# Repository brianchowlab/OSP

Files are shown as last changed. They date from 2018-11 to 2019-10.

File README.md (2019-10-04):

# OSP: An Open-source Plate Reader 
<p align="center">
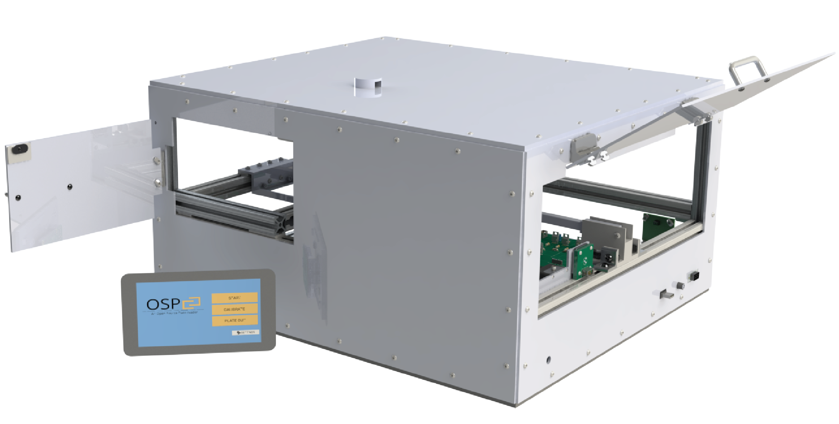
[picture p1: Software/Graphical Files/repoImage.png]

</p>

## Introduction
OSP is a low-cost open-source plate reader built out of the [Chow Lab](http://chowlab.seas.upenn.edu/) and the [George H. Stephenson Foundation Bioengineering Educational Laboratory & Bio-MakerSpace](https://belabs.seas.upenn.edu/) at the University of Pennsylvania. The software provided in this repository is required to access the full functionailty of a built OSP device. For information regarding how to build this device and details about how it works, please refer to the ACS: BioChemistry manuscript available at this [LINK](https://www.biorxiv.org/content/early/2018/09/12/413781).

## Contents
The repository is divided into two main components: (1) Hardware & (2) Software
        
* [**HARDWARE**](https://github.com/brianchowlab/OSP/tree/master/Hardware)

    All the files required for assembly of the OSP device are in this folder. All the instructions on how to assemble the OSP device can be found in the *ASSEMBLY FILES* directory.
  * [***CAD FILES***](https://github.com/brianchowlab/OSP/tree/master/Hardware/CAD%20Files)
  * [***LASER CUT FILES***](https://github.com/brianchowlab/OSP/tree/master/Hardware/Laser%20Cut%20Files)
  * [***PCB FILES***](https://github.com/brianchowlab/OSP/tree/master/Hardware/PCB%20Files)
  * [***ASSEMBLY FILES***](https://github.com/brianchowlab/OSP/tree/master/Hardware/Assembly%20Files)
* [**SOFTWARE**](https://github.com/brianchowlab/OSP/tree/master/Software)

    All the files for installation and execution of the OSP software are in this folder. The full *Software Guide* can be found here as a PDF.
  * [***ARDUINIO FILES***](https://github.com/brianchowlab/OSP/tree/master/Software/Arduino%20Files/OSP_Serial_Communication/COPR_Serial_Communication)
  * [***GRAPHICAL FILES***](https://github.com/brianchowlab/OSP/tree/master/Software/Graphical%20Files)
  * [***PYTHON FILES***](https://github.com/brianchowlab/OSP/tree/master/Software/Python%20Files)
    * Data - Folder where all data from the OSP device is saved as .xlsx files.
    * Protocols - Folder where any protocol sequence is saved. 
    * Screens - Python files for all GUI screens
    * System Settings - Folder where are all files associated with settings are contained.
    * Raspberry Pi Image - Contains the link to the Raspberry-Pi image file.

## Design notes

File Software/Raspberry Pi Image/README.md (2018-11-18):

# OSP: An Open-source Plate Reader 

## RASBPERRY PI IMAGE - LINK BELOW 

[DISK IMAGE FILE (Updated Nov. 18, 2018)](https://www.dropbox.com/s/7g2e63knupe5y7j/osp_rasp.img?dl=0)

## Instructions for referrence:

### Installation (Raspberry-Pi Image)
The simplest way to install the OSP software on a Raspberry-Pi is by downloading and installing the OSP.img file provided. In order to do this, you will need to have a completely empty 16GB Micro SD Card. If the card is not empty, all of its contents will be deleted in the installation of the OSP.img file. In addition, the first 3 installation steps need to be performed on a computer/laptop with an SD card slot. 

**Step 1.** *Download & Unzip the OSP.img* - Visit the following [LINK](https://www.dropbox.com/s/7g2e63knupe5y7j/osp_rasp.img?dl=0) and download the *OSP.img* file. Once downloaded unzip the file to a known location. 

**Step 2.** *Download & Install the Etcher program* - Visit the following [LINK](https://www.balena.io/etcher/) and download the *Etcher* program for your specific operating system. 

**Step 3.** *Install the OSP.img onto the SD Card* - Insert your empty SD card into the computer. Start up the Etcher software and follow the on screen instructions in order to install the OSP.img onto the card. **This process can take up to 10 minutes**

**Step 4.** *Update OSP repository* - Once the OSP.img file is installed, insert it into your Raspberry-Pi (which should be connected to the active OSP device, touch-screen/monitor, keyboard & mouse). Turn the Raspberry-Pi on and when it is booted open up the Terminal. Type the following and close the Terminal when it is finished:
```sh
$ cd OSP
$ git pull origin master
```
**Step 5.** *Running the Usert Interface* - To activate the User Interface make sure the OSP device is turned on and connected to the Raspberry-Pi via USB. Open up the Terminal and type the following:
```sh
$ cd  "OSP\Software\Python Files"
$ sudo python GUI.py
```
## SOFTWARE - Before Running a Protocol

### Initial Functionality Testing
Once you have completed the installation process (by following the steps above) it is usefull to check if all the light sources (LEDs) and linear actuators as behaving correctly. These tests can be performed from the Arduino IDE *Serial Monitor*. 

**Step 1.** *Open Arduino Serial Monitor* - Make sure the OSP device is plugged into a computer/Raspberry-Pi and turned on. Open up the Arduino IDE and click on the ***Tools*** tab in the menu bar. From the dropdown menu select ***Serial Monitor***. This will open up the ***Serial Monitor*** in a new window. 

**Step 2.** *Test Linear Actuator Functionality* 
* Type the following into the text box at the top of the Serial Monitor and press the *Send* button: **M1500.001500.00;** 
  * This should extend both linear actuators about half way. 
* Type the following into the text box at the top of the Serial Monitor and press the *Send* button: **M1000.001000.00;** 
  * This should retract both linear actuators all the way. 
  
**Step 3.** *Test LED Functionality* 
* Type the following into the text box at the top of the Serial Monitor and press the *Send* button: **L1;** 
  * This should result in the LED 1 turning on. To turn it off, type the same command in again.   
* Type the following into the text box at the top of the Serial Monitor and press the *Send* button: **L2;** 
  * This should result in the LED 2 turning on. To turn it off, type the same command in again.   
* Type the following into the text box at the top of the Serial Monitor and press the *Send* button: **L3;** 
  * This should result in the LED 3 turning on. To turn it off, type the same command in again.
* Type the following into the text box at the top of the Serial Monitor and press the *Send* button: **L4;** 
  * This should result in the LED 4 turning on. To turn it off, type the same command in again.
* Type the following into the text box at the top of the Serial Monitor and press the *Send* button: **L5;** 
  * This should result in the LED 5 & LED 6 (top) turning on. To turn them off, type the same command in again.
  
### Calibration Guide
The software provided in this repository comes with pre-loaded with calibrated positions for a 24-well plate and a 96-well plate. However, it is recommended that an initial calibration is performed after the OSP device is built to account for any small differences in assembly. 

Before performing any sort of calibration you will need to prepare the calibration lid for the specific plate-type that is to be calibrated. Refer to the *Calibration Lid Assembly* at the end of the *General Assembly Guide* for instructions on how to do this.

The following steps should be followed everytime a calibration is performed:

**Step 1.** *Attach Fiber to Photodiode* - Deattach the fiber from the STS spectrophotometer and screw it into the photodiode mount rigth next to it. 

**Step 2.** *Adjust the Iris* -  As part of the Top Optics assembly there is an iris. Using the guidelines on the rim of the iris, set the iris to a size of 2. 

**Step 3.** *Insert plate into OSP device* - Place the calibration lid onto an empty micro-well plate and insert it into the device, such that well A1 is in the top left corner of the plate holder. (To move the plate holder near the door, press the *plate out* button on the GUI). 

**Step 4.** *Initialize calibration* - On the GUI press the *Calibrate* button and when prompted input the size of the micro-well plate (24 or 96). The machine will begin the calibration process and alert you when it is finished. **This process takes around 3 minutes**

### Loading a Plate

The orientation in which you load the plate is important not only for the calibration process but also for any sort of measurement performed on the OSP device. Please refer to the below picture to ensure you are loading the plate correctly.  The plate should be held firmly in place with attached springs. 
<p align="center">
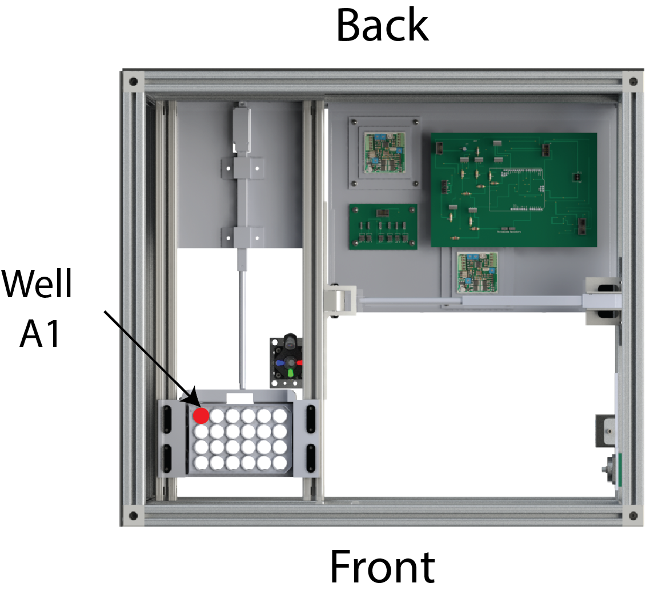
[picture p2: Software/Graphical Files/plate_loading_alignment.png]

</p>

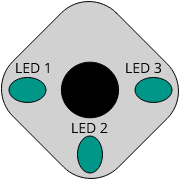
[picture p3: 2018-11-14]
Software/PythonFiles/Images/botttomLed.png

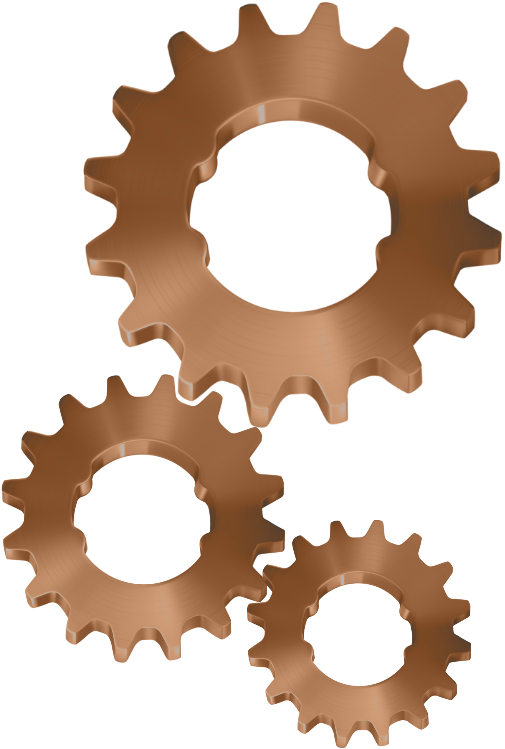
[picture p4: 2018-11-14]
Software/PythonFiles/Images/copr_gears.png

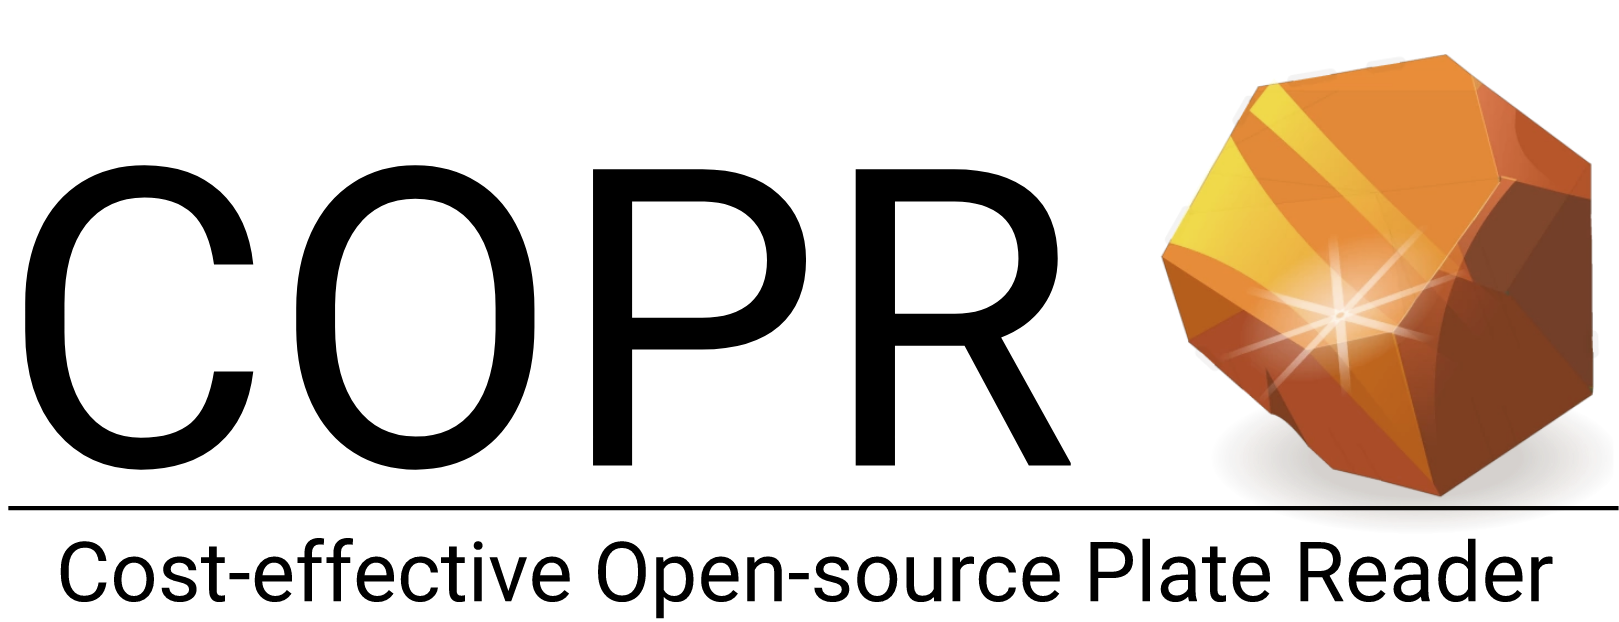
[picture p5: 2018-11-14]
Software/PythonFiles/Images/Page 3.png

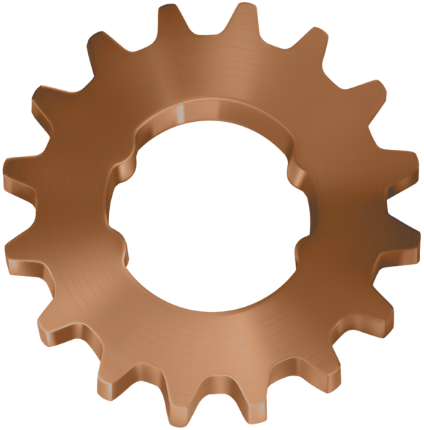
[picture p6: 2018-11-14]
Software/PythonFiles/Images/copr_gears_v2.png

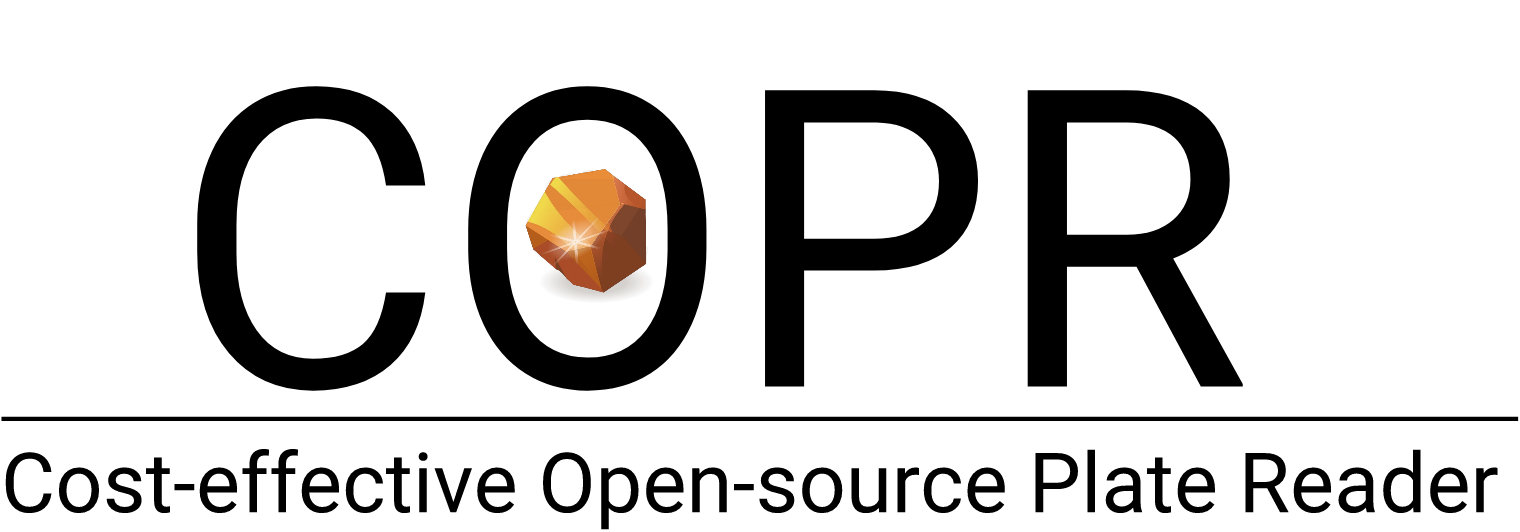
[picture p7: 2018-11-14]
Software/PythonFiles/Images/Page 6.png

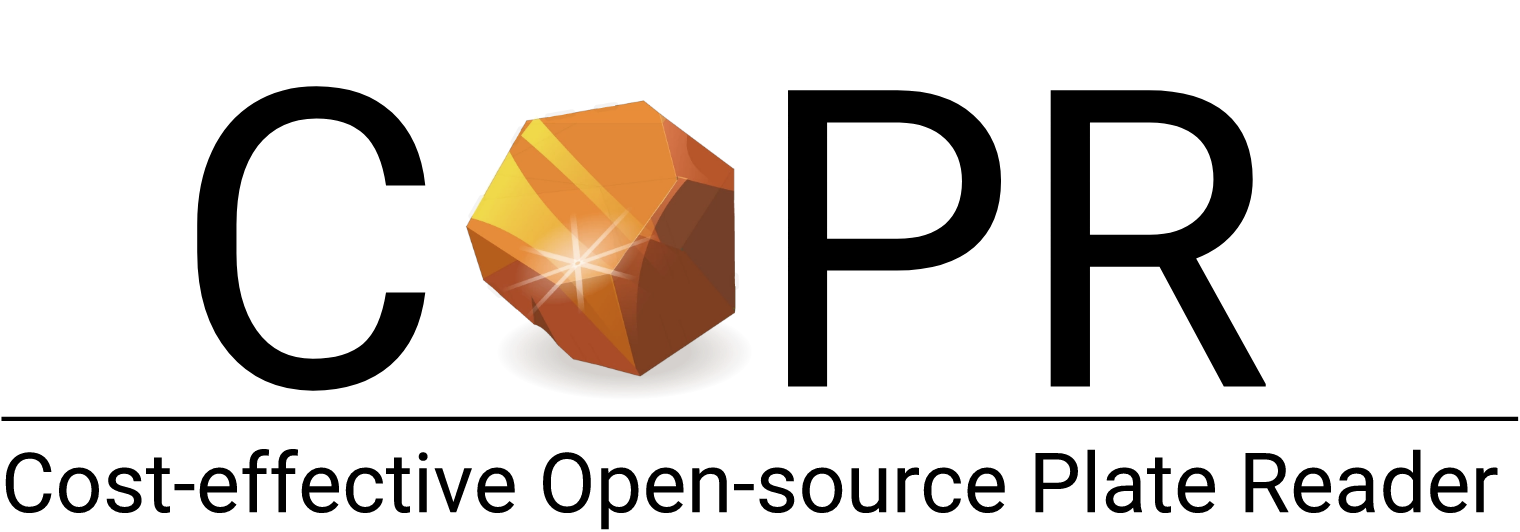
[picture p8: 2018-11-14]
Software/PythonFiles/Images/Page 5.png

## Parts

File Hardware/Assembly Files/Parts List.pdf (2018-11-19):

TABLE S1. OSP component list and costs. The total instrument cost is <$3,500. Laser cut and 3D-printed costs are reflected in material costs.
Key: Blue = optics (O). Gray = Frame (F). Orange = Electronics (E). Green = Laser Cut (L). Pink = 3D Print (P).
# | Vendor | Part Description | Part / Model Number | Unit cost | Number | Line subtotal

O1 | Thorlabs | Universal Base Plate, 2.5" x 2.5" x 3/8" | UBP2 | $36.47 | 2 | $72.94
O2 | Thorlabs | Cage Assembly Rod, 4" Long, Ø6 mm | ER4 | $7.10 | 1 | $7.10
O3 | Thorlabs | Cage Assembly Rod, 3" Long, Ø6 mm | ER3 | $6.60 | 1 | $6.60
O4 | Thorlabs | SM1-Threaded 30 mm Cage Plate, 6 mm Thick | CP6S | $19.16 | 2 | $38.32
O5 | Thorlabs | Aspheric Condenser Lens, Ø12 mm, f=10.5 mm, NA=0.54, Uncoated | ACL1210U | $18.05 | 2 | $36.10
O6 | Thorlabs | SM05 Lens Tube, 0.50" Thread Depth, One Retaining Ring Included | SM05L05 | $14.10 | 3 | $42.30
O7 | Thorlabs | Adapter with External SM1 Threads and Internal SM05 Threads, Knurled Edge | SM1A6FW | $19.99 | 2 | $39.98
O8 | Thorlabs | SM1 Graduated Ring-Actuated Iris Diaphragm (Ø1 - Ø12 mm) | SM1D12C | $103.02 | 1 | $103.02
O9 | Thorlabs | SM1 Lens Tube, 2" Thread Depth, One Retaining Ring Included | SM1L20 | $16.50 | 1 | $16.50
O10 | Thorlabs | LED Socket | 8060-2 | $9.89 | 5 | $49.45
O11 | Thorlabs | SM05-Threaded Mount for TO-18, TO-39, TO-46, or T-1 3/4 LEDs | S05LEDM | $32.64 | 1 | $32.64
O12 | Thorlabs | SMA Fiber Adapter Plate with External SM1 (1.035"-40) Thread | SM1SMA | $29.58 | 2 | $59.16
O13 | Thorlabs | SM1-Threaded Aluminum Mount for TO-5 Laser Diodes | S1LM05 | $36.47 | 1 | $36.47
O14 | Thorlabs | LED with a Glass Lens, 430 nm, 8 mW, TO-18 | LED430L | $11.73 | 1 | $11.73
O15 | Thorlabs | Epoxy-Encased White Light LED, 13.0 mW, 7.5° Half Viewing Angle, Qty. of 5 | LEDWE-15 | $9.38 | 1 | $9.38
O16 | Thorlabs | 543 nm, f = 7.86 mm, NA = 0.51 SMA905 Fiber Collimation Pkg. | F240SMA-A | $150.96 | 1 | $150.96
O17 | Thorlabs | 1/4"-20 Low-Profile Channel Screws (100 Screws/Box) | SH25LP38 | $23.66 | 1 | $23.66
O18 | Thorlabs | Drop-In T-Nut, 1/4"-20 Tapped Hole | XE25T1 | $29.33 | 1 | $29.33
O19 | Thorlabs | Si Photodiode, 10 ns Rise Time, 350 - 1100 nm, 3.6 mm x 3.6 mm Active Area | FDS100 | $14.08 | 1 | $14.08
O20 | Thorlabs | SM05 Lens Tube, 2" Thread Depth, One Retaining Ring Included | SM05L20 | $20.60 | 1 | $20.60
O21 | Thorlabs | OEM Flange to Internal SM1 Adapter, 10 mm Thread Depth | SM1F1 | $19.18 | 1 | $19.18
O22 | LED Supply | 5mm LED - Blue 470nm 15 Degree Viewing Angle | L1-0-B5TH15-1 | $0.47 | 1 | $0.47
O23 | LED Supply | 5mm LED - Orange 610nm 30 Degree Viewing Angle | L4-0-O5TH30-1 | $0.60 | 1 | $0.60
O24 | LED Supply | 5mm LED - Green 525nm 15 Degree Viewing Angle | L1-0-G5TH15-1 | $0.49 | 1 | $0.49
O25 | Ocean Optics | STS-VIS Spec (Included fiber) | STS-VIS | $1,000.00 | 1 | $1,000.00
F1 | 80/20 | 1.00” X 1.00” T-Slotted Profile - Four Open T-Slots (19 inch, 2x End Tap) | 1010 | $10.22 | 5 | $51.10
F2 | 80/20 | 1.00” X 1.00” T-Slotted Profile - Four Open T-Slots (19 inch, Counter-bore) | 1010 | $15.32 | 3 | $45.96
F3 | 80/20 | 1.00” X 1.00” T-Slotted Profile - Four Open T-Slots (22 inch, 2x End Tap) | 1010 | $10.91 | 6 | $65.46
F4 | 80/20 | 1.00” X 1.00” T-Slotted Profile - Four Open T-Slots (10 inch, 2x End Tap) | 1010 | $4.25 | 4 | $17.00
F5 | 80/20 | 1.00” X 1.00” T-Slotted Profile - Four Open T-Slots (8 inch, 2x End Tap) | 1010 | $3.79 | 2 | $7.58
F6 | 80/20 | 10 Series 3 Way - Squared Corner Connector | 4042-Black | $19.21 | 8 | $153.68

S1

F7 | 80/20 | 10 Series 4 Hole - Detent Hinge | 2071 | $14.45 | 3 | $43.35
F8 | 80/20 | 10 & 15 Series Magnetic Door Catch | 2090 | $6.85 | 1 | $6.85
F9 | 80/20 | 10 Series 10-32 Short Double Anchor Assembly | 3091 | $5.25 | 6 | $31.50
F10 | 80/20 | 10 Series 2 Hole - Inside Corner Bracket | 4119 | $2.90 | 6 | $17.40
F11 | 80/20 | 1/4-20 x .500" Button Head Socket Cap Screw (BHSCS) | 3061 | $0.23 | 22 | $5.06
F12 | 80/20 | 1/4-20 Slide-in Economy T-Nut - Centered Thread | 3382 | $0.21 | 20 | $4.20
F13 | 80/20 | 10 & 25 Series 10-32 Standard Drop-in T-Nut | 14162 | $0.68 | 200 | $136.00
F14 | 80/20 | 10 Series 90 Degree Structural Pivot Nub | 4188 | $4.60 | 1 | $4.60
F15 | 80/20 | 1/4-20 x 1.000" Low Head Socket Cap Screw (LHSCS) | 3017 | $0.53 | 28 | $14.84
F16 | 80/20 | Steel Door Handle | 2070 | $4.45 | 2 | $8.90
F17 | 80/20 | 8-32 Double Slide-in Economy T-Nut | 3281 | $0.69 | 4 | $2.76
F18 | 80/20 | 10 Series Single-Keyed UniBearing™ Pad | 6705 | $2.05 | 9 | $18.45
F19 | McMaster-Carr | Passivated 18-8 Stainless Steel, M4 x 0.70 mm Thread, 10mm Long (100 pack) | 92095A190 | $9.05 | 2 | $18.10
F20 | McMaster-Carr | Scratch-Resistant Acrylic - Black, 12" x 24" x 1/8" | 8505K742 | $14.75 | 6 | $88.50
F21 | McMaster-Carr | Scratch-Resistant Acrylic - Black, 12" x 24" x 1/4" | 8505K755 | $19.93 | 2 | $39.86
F22 | McMaster-Carr | Medium-Strength Steel Hex Nut (100 pack) | 95462A029 | $4.40 | 1 | $4.40
F23 | McMaster-Carr | Button Head Hex Drive Screw, Passivated 18-8 Stainless Steel, M3 x 0.50 mm Thread, 16mm Long (100 pack) | 92095A184 | $8.85 | 1 | $8.85
F24 | McMaster-Carr | Zinc-Plated Steel Hex Nut, Medium-Strength, Class 8, M2.5 x 0.45 mm Thread (100 pack) | 90591A270 | $2.22 | 1 | $2.22
F25 | McMaster-Carr | Zinc-Plated Steel Hex Nut, Medium-Strength, Class 8, M4 x 0.7 mm Thread (100 pack) | 90591A255 | $2.35 | 1 | $2.35
F26 | McMaster-Carr | Button Head Hex Drive Screw, Passivated 18-8 Stainless Steel, M4 x 0.70 mm Thread, 14mm Long (50 pack) | 92095A193 | $8.16 | 1 | $8.16
F27 | McMaster-Carr | High-Strength Steel Nylon-Insert Locknut, Class 10, Zinc-Plated, M4 x 0.7 mm Thread (10 pack) | 94645A101 | $10.62 | 1 | $10.62
F28 | McMaster-Carr | 18-8 Stainless Steel Hex Nut, 4-40 Thread Size (100 pack) | 91841A005 | $2.91 | 1 | $2.91
F29 | McMaster-Carr | 18-8 Stainless Steel Button Head Hex Drive Screw, 4-40 Thread Size, 3/4" Long (100 pack) | 92949A113 | $4.03 | 1 | $4.03
F30 | McMaster-Carr | Passivated 18-8 Stainless Steel Pan Head Phillips Screws, M4 x 0.7mm Thread, 25mm Long (100 pack) | 92000A230 | $10.34 | 1 | $10.34
F31 | McMaster-Carr | Button Head Hex Drive Screw, Passivated 18-8 Stainless Steel, M2.5 x 0.45 mm Thread, 10mm Long (25 pack) | 92095A460 | $8.51 | 1 | $8.51
F32 | McMaster-Carr | 18-8 Stainless Steel Button Head Hex Drive Screw, 4-40 Thread Size, 1/4" Long (100 pack) | 92949A106 | $2.87 | 1 | $2.87
F33 | McMaster-Carr | 18-8 Stainless Steel Pan Head Slotted Screws, 2-56 Thread Size, 3/8" Long | 91792A079 | $4.33 | 1 | $4.33
F34 | McMaster-Carr | Passivated 18-8 Stainless Steel Phillips Flat Head Screw, M3 x 0.5 mm Thread, 5 mm Long (100 pack) | 92010A114 | $3.92 | 1 | $3.92

F35 | Amazon | Hilitchi 250-Pcs M2 / M3 /M4 Female Thread Brass Knurled Threaded Insert Embedment Nuts Assortment Kit | ASIN: B0784VYCYY | $19.88 | 1 | $19.88
F36 | Amazon | Neiko 50456A Spring Assortment Kit for Repairs, Steel Zinc Plated | 200-Piece Set. | ASIN: B000K7M36W | $8.49 | 1 | $8.49
F37 | MakerBot | True Black PLA Large Spool / 1.75mm / 1.8mm Filament | -- | $48.00 | 1 | $48.00
E1 | Actuonix | Linear Actuator Control Board | LAC | $40.00 | 2 | $80.00
E2 | Actuonix | L16-P Linear Actuator with Feedback (140mm Stroke Length, 63:1 Gear Ratio) | L16-P | $80.00 | 2 | $160.00
E3 | Arduino | Arduino-UNO | A000066 | $22.00 | 1 | $22.00
E4 | Adafruit | Raspberry Pi 3 - Model B+ - 1.4GHz Cortex-A53 with 1GB RAM | Website: 3775 | $35.00 | 1 | $35.00
E5 | Raspberry-Pi | Raspberry Pi Touch Display | Touch Display | $59.99 | 1 | $59.99
E6 | Amazon | Case for the Official Raspberry Pi 7" Touchscreen Display - Adjustable angle | ASIN: B01HV97F64 | $27.99 | 1 | $27.99
E7 | Amazon | LEDMO Power Supply, Transformers,LED Adapter, 12V, 5A Max | ASIN: B01461MOGQ | $10.99 | 1 | $10.99
E8 | Amazon | IDC Serial to Panel Mount Serial Cable (PNL9M16) | ASIN: B0067DB6RU; OEM: PNL9M16 | $6.27 | 1 | $6.27
E9 | Amazon | Raspberry Pi 3 Model B Power Charger 5V 2.5A Power Adapter Micro Cable | ASIN: B07BKSLGYX | $8.55 | 2 | $17.10
E10 | Amazon | USB3.0 Coupler Female to Female Adapter | ASIN: B0B:C0J4NMTMQ | $7.99 | 1 | $7.99
E11 | Amazon | AmazonBasics 4-Port USB 2.0 Ultra-Mini Hub | ASIN: B003M0NURK | $6.99 | 1 | $6.99
E12 | Amazon | JST Conenctor Kit | ASIN: B0731MZCGF | $13.87 | 1 | $13.87
E13 | Amazon | Pc Accessories 50-PACK IDC 2X3 6 Pins Dual Row Sockets for Flat Ribbon Cable, 6P 2.54mm FC Female Connectors | ASIN: B00T9BJGRE | $12.95 | 1 | $12.95
E14 | Amazon | Case for The Official Raspberry Pi 7" Touchscreen Display - Adjustable Angle | ASIN: B01HV97F64 | $24.99 | 1 | $24.99
E15 | Mouser | IRF520NPBF - Mosfet | IRF520NPBF | $0.98 | 6 | $5.88
E16 | Sparkfun | Voltage Regulator - 5V - STMicroelectronics L7805CV | COM-00107; OEM: L7805CV | $0.95 | 1 | $0.95
E17 | Sparkfun | 2x3 Pin Shrouded Header | PRT-10877 | $1.50 | 4 | $6.00
E18 | Sparkfun | 2x5 Pin Shrouded Header | PRT-08506 | $1.50 | 1 | $1.50
E19 | Sparkfun | Rocker Switch - SPST (right-angle) | COM-08837 | $0.95 | 1 | $0.95
E20 | Sparkfun | DC Barrel Jack Adapter - Female | PRT-10288 | $2.95 | 1 | $2.95
E21 | Sparkfun | Break Away Headers - Straight (40 count) | PRT-00116 | $1.50 | 2 | $3.00
E22 | Sparkfun | Photon Stackable Header - 12 Pin | PRT-14322 | $0.50 | 2 | $1.00
E23 | Sparkfun | Screw Terminals 3.5mm Pitch (2-Pin) | PRT-08084 | $0.95 | 2 | $1.90
E24 | Mouser | Various Resistors (1kOhm, 330Ohm, 100MOhm) | FMP200JR-52-1K | $0.20 | 15 | $3.00
E25 | Mouser | .1uF Capacitor | FA24NP02E103JNU06 | $0.61 | 1 | $0.61
E26 | 4PCB | Custom Made PCBs - Main Power Board | -- | $47.51 | 1 | $47.51
E27 | 4PCB | Custom Made PCBs - Power-switch Board | -- | $24.56 | 1 | $24.56
E28 | 4PCB | Custom Made PCBs - LED Circuit | -- | $26.63 | 1 | $26.63
E29 | 4PCB | Custom Made PCBs - Photodiode Circuit | -- | $25.24 | 1 | $25.24
L1 | Laser Cut | Part #L1 - Front Floor | -- | -- | -- | --

L2 | Laser Cut | Part #L2 - Back Floor | -- | -- | -- | --
L3 | Laser Cut | Part #L3 - Front Panel | -- | -- | -- | --
L4 | Laser Cut | Part #L4 - Back Panel | -- | -- | -- | --
L5 | Laser Cut | Part #L5 - Right Panel | -- | -- | -- | --
L6 | Laser Cut | Part #L6 - Right Panel Door | -- | -- | -- | --
L7 | Laser Cut | Part #L7 - Front Panel Door | -- | -- | -- | --
L8 | Laser Cut | Part #L8 - Front Top Panel | -- | -- | -- | --
L9 | Laser Cut | Part #L9 - Back Top Panel | -- | -- | -- | --
L10 | Laser Cut | Part #L10 - Y-Axis Motor Floor | -- | -- | -- | --
L11 | Laser Cut | Part #L11 - Primary Electronics Mount | -- | -- | -- | --
L12 | Laser Cut | Part #L12 - Detector Wall Mount | -- | -- | -- | --
L13 | Laser Cut | Part #L13 - LAC Board Panel Mount | -- | -- | -- | --
L14 | Laser Cut | Part #L14 - LAC Alignment Frame | -- | -- | -- | --
L15 | Laser Cut | Part #L15 - External Device Plate | -- | -- | -- | --
L16 | Laser Cut | Part #L16 - Top Optics LED Insert Tab | -- | -- | -- | --
L17 | Laser Cut | Part #L17 - Top Optics LED Cage Aligner | -- | -- | -- | --
L18 | Laser Cut | Part #L18 - 24-Well Calibration Lid | -- | -- | -- | --
L19 | Laser Cut | Part #L19 - 96-Well Calibration Lid | -- | -- | -- | --
L20 | Laser Cut | Part #L20 - Left Panel | -- | -- | -- | --
P1 | 3D Print | Part #P1 - X-Axis Motor Holder | -- | -- | -- | --
P2 | 3D Print | Part #P2 - Y-Axis Motor Tab | -- | -- | -- | --
P3 | 3D Print | Part #P3 - Plate Holder | -- | -- | -- | --
P4 | 3D Print | Part #P4 - PCB Stability Columns | -- | -- | -- | --
P5 | 3D Print | Part #P5 - Excitation LED Mount | -- | -- | -- | --
P6 | 3D Print | Part #P6 - Top Auxiliary Plug | -- | -- | -- | --
P7 | 3D Print | Part #P7 - Wire Holder | -- | -- | -- | --
| Amazon | Alternative to #P7: Adhesive Cable Clips | ASIN: B01HR9VS4I | $6.39 | 1 | $6.39
P8 | 3D Print | Part #P8 - 24-Well Calibration Lid Plug | -- | -- | -- | --
P9 | 3D Print | Part #P9 - 96-Well Calibration Lid Plug | -- | -- | -- | --
P10 | 3D Print | Part #P10 - X-Motor Stabilizer | -- | -- | -- | --
| | | | | TOTAL | $3,396.29

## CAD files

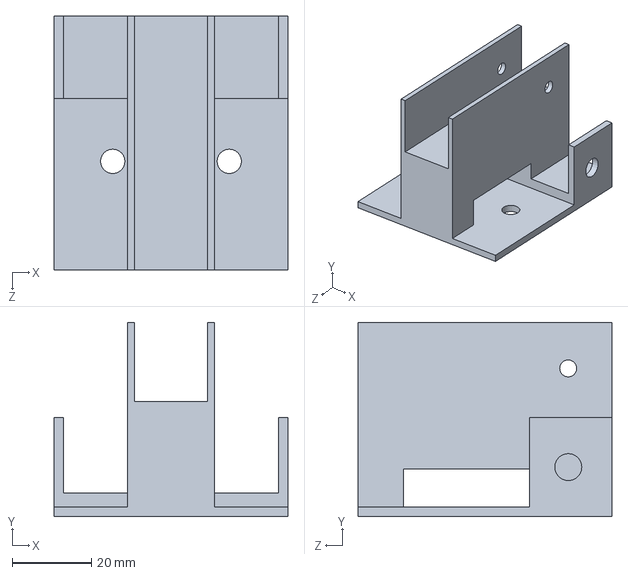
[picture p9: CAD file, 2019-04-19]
Hardware/CAD Files/P1 - X-Axis Motor Holder/P1 - X-Axis Motor Holder.SLDPRT
59.0 x 49.0 x 64.0 mm

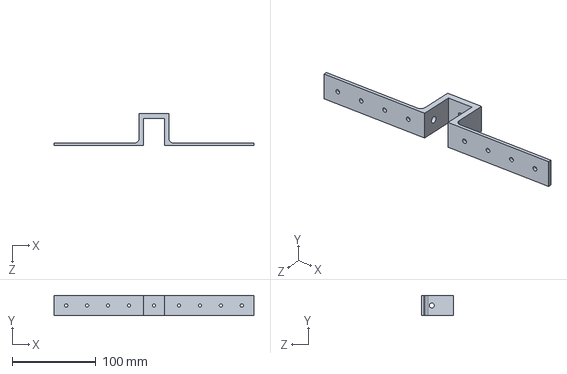
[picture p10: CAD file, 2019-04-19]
Hardware/CAD Files/P10 - X-Motor Stabilizer/P10 - X-Motor Stabilizer.SLDPRT
239.2 x 24.0 x 38.5 mm

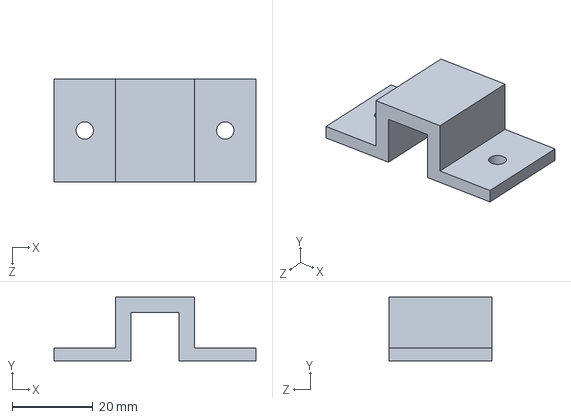
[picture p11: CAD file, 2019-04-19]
Hardware/CAD Files/P2 - Y-Axis Motor Tab/P2 - Y-Axis Motor Tab.SLDPRT
50.0 x 15.7 x 25.4 mm

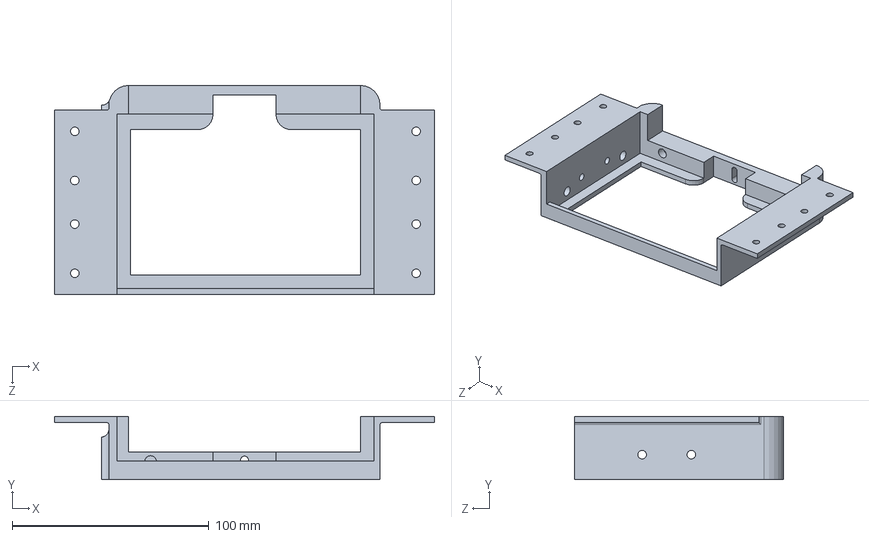
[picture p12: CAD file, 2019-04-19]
Hardware/CAD Files/P3 - Plate Holder/P3 - Plate Holder.SLDPRT
193.2 x 32.2 x 106.3 mm

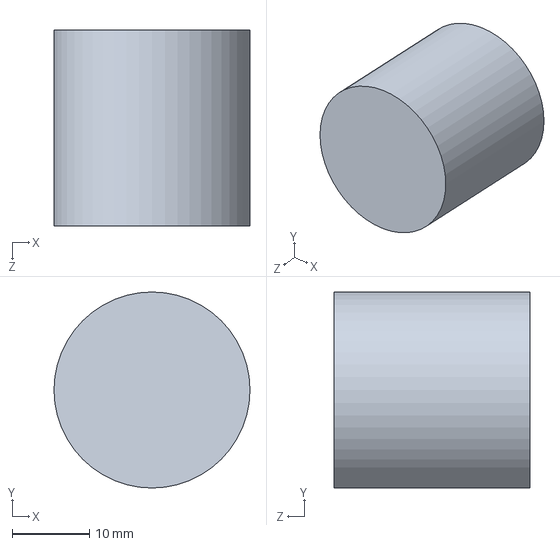
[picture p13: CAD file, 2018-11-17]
Hardware/CAD Files/P4 - PCB Stability Column/P4 - PCB Stability Column.SLDPRT
25.4 x 25.4 x 25.4 mm

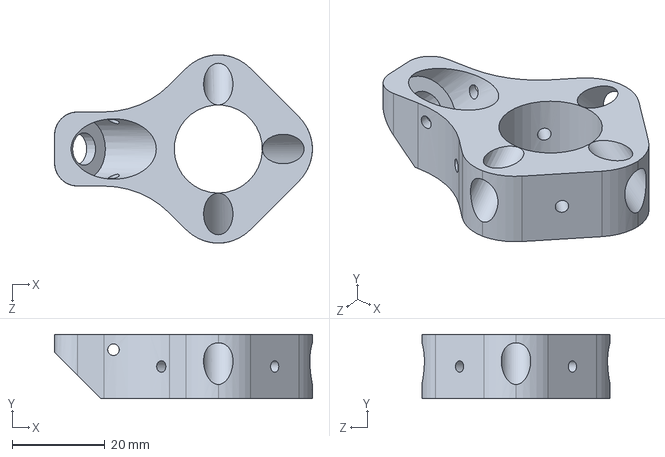
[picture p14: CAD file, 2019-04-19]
Hardware/CAD Files/P5 - Excitation LED Mount/P5 - Excitation LED Mount.SLDPRT
55.6 x 13.9 x 40.6 mm

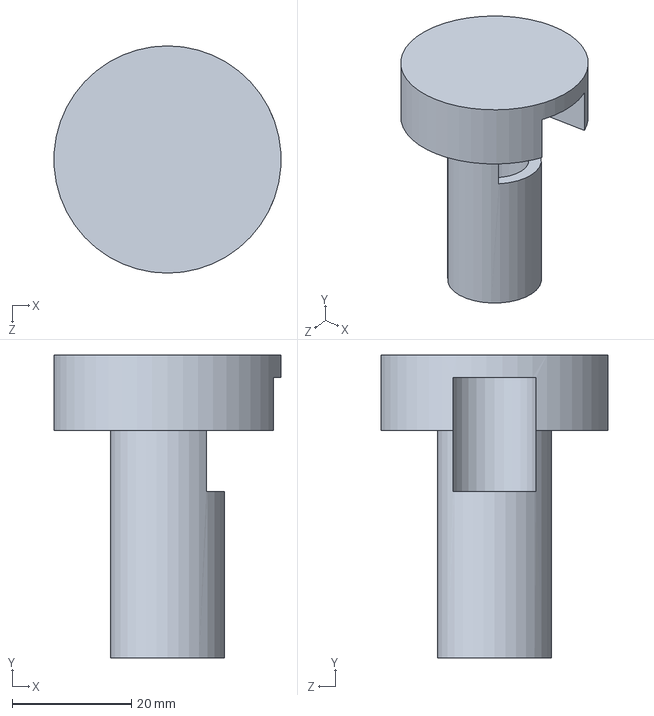
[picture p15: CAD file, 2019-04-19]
Hardware/CAD Files/P6 - Top Auxiliary Plug/P6 - Top Auxiliary Plug.SLDPRT
38.0 x 50.8 x 38.1 mm

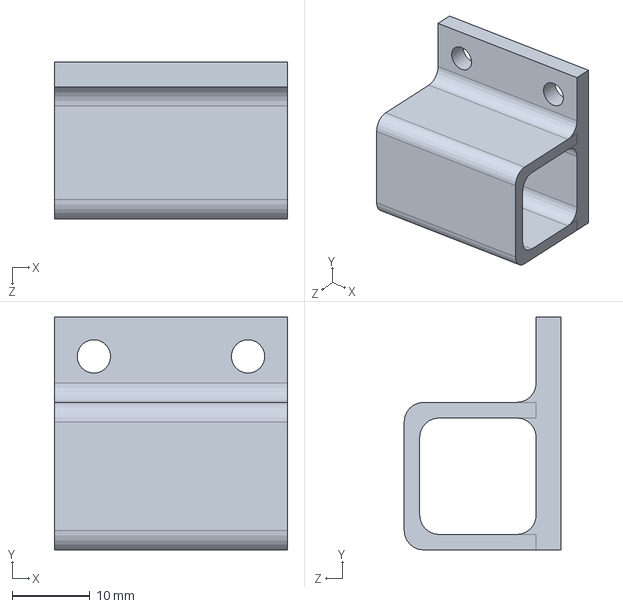
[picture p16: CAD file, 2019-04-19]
Hardware/CAD Files/P7 - Wire Holder/P7 - Wire Holder.SLDPRT
30.0 x 30.0 x 20.2 mm

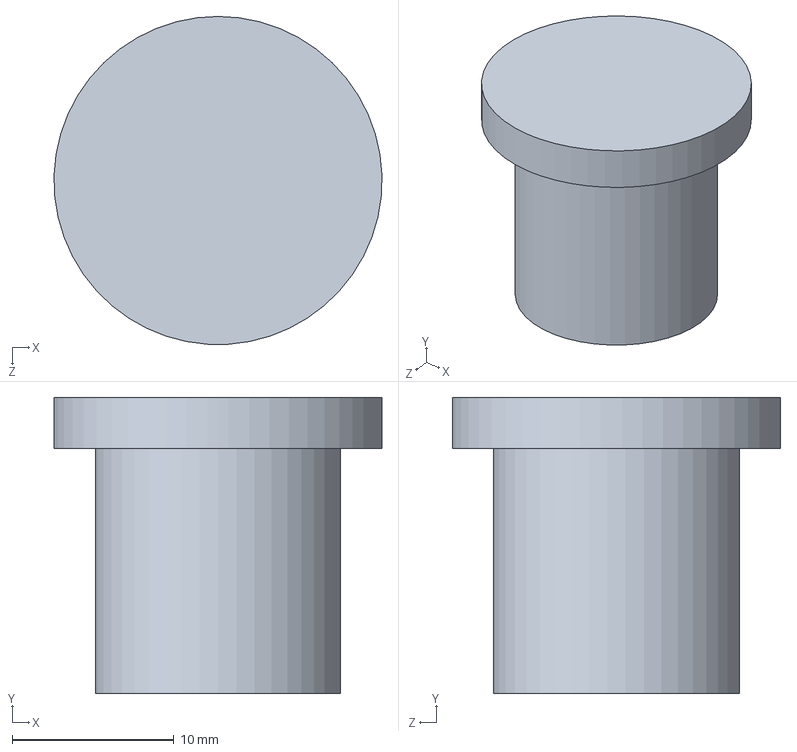
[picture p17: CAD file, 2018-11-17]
Hardware/CAD Files/P8 - 24-Well Calibration Plug/P8 - 24-Well Calibration Plug.SLDPRT
20.3 x 18.4 x 20.3 mm

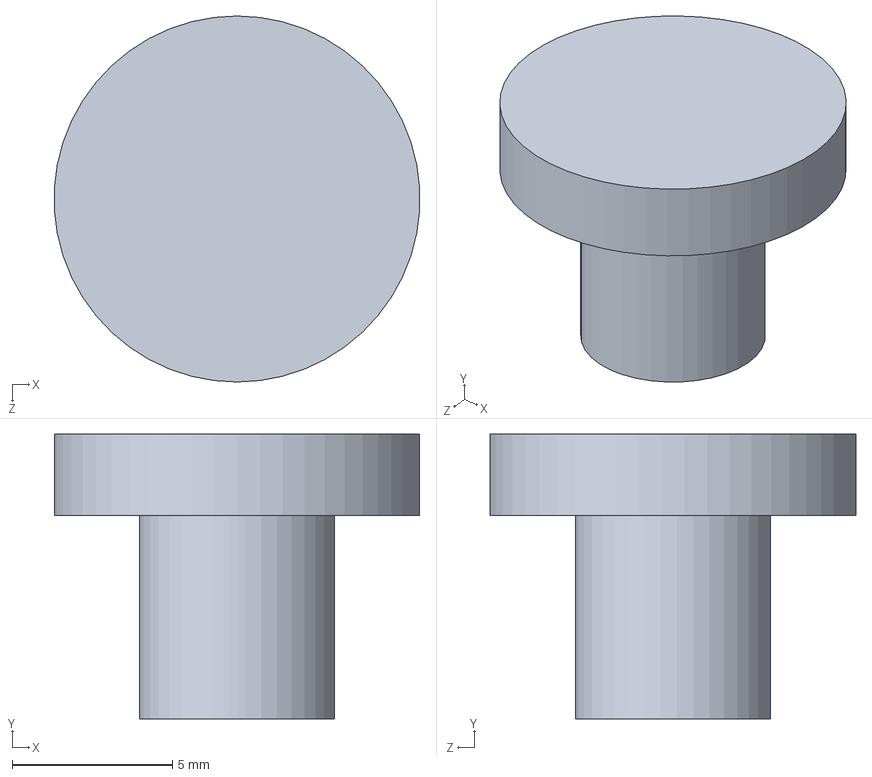
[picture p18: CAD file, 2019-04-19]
Hardware/CAD Files/P9 - 96-Well Calibration Plug/P9 - 96-Well Calibration Plug.SLDPRT
11.4 x 8.89 x 11.4 mm

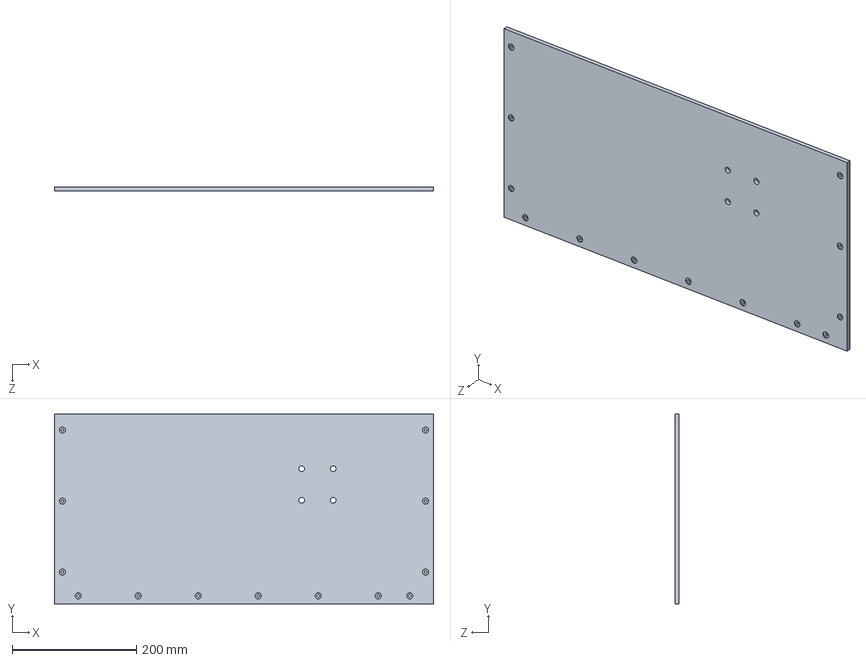
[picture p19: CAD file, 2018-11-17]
Hardware/Laser Cut Files/L1 - Front Floor/L1 - Front Floor.SLDPRT
609.6 x 304.8 x 6.35 mm

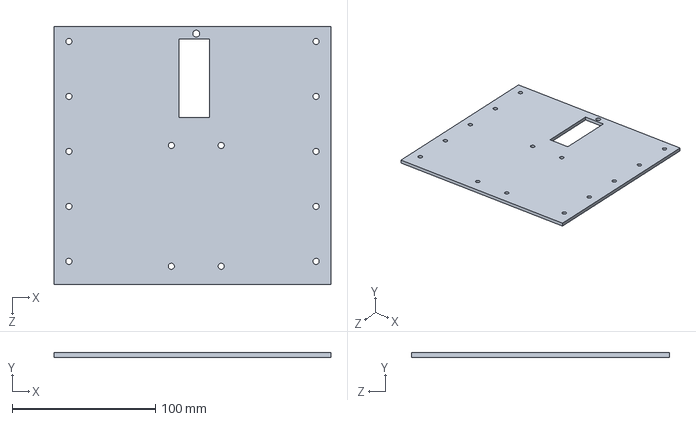
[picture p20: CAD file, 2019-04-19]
Hardware/Laser Cut Files/L10 - Y-Axis Motor Floor/L10 - Y-Axis Motor Floor.SLDPRT
193.3 x 3.17 x 180.0 mm

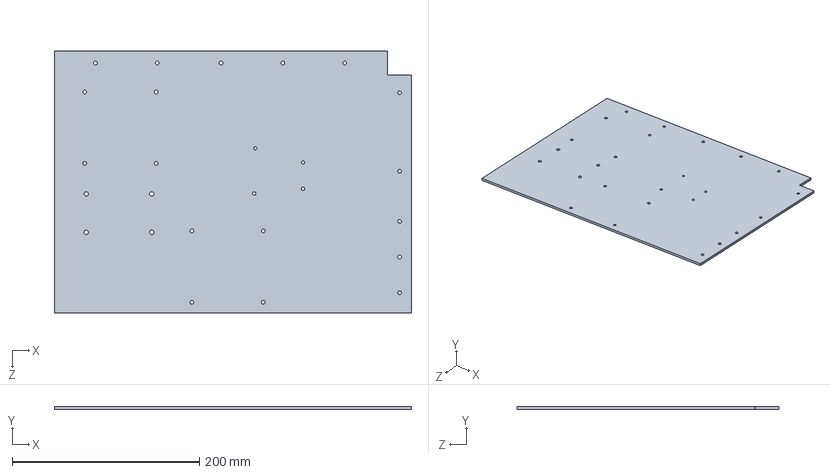
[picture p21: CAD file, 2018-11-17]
Hardware/Laser Cut Files/L11 - Primary Electronics Mount/L11 - Primary Electronics Mount.SLDPRT
381.0 x 3.17 x 279.4 mm

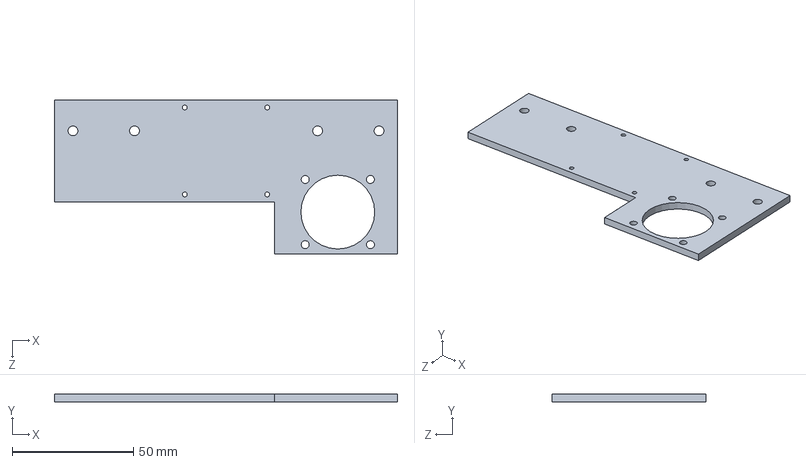
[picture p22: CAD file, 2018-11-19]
Hardware/Laser Cut Files/L12 - Detector Wall Mount/L12 - Detector Wall Mount.SLDPRT
141.6 x 3.17 x 63.5 mm

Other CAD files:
Hardware/Laser Cut Files/L13 - LAC Board Panel Mount/L13 - LAC Board Panel Mount.SLDPRT
Hardware/Laser Cut Files/L14 - LAC Alignment Frame/L14 - LAC Alignment Frame.SLDPRT
Hardware/Laser Cut Files/L15 - External Device Plate/L15 - External Device Plate.SLDPRT
Hardware/Laser Cut Files/L16 - Top Optics LED Insert Tab/L16 - Top Optics LED Insert Tab.SLDPRT
Hardware/CAD Files/P1 - X-Axis Motor Holder/P1 - X-Axis Motor Holder.STL
Hardware/CAD Files/P10 - X-Motor Stabilizer/P10 - X-Motor Stabilizer.STL
Hardware/CAD Files/P2 - Y-Axis Motor Tab/P2 - Y-Axis Motor Tab.STL
Hardware/CAD Files/P3 - Plate Holder/P3 - Plate Holder.STL
Hardware/CAD Files/P4 - PCB Stability Column/P4 - PCB Stability Column.STL
Hardware/CAD Files/P5 - Excitation LED Mount/P5 - Excitation LED Mount.STL
Hardware/CAD Files/P6 - Top Auxiliary Plug/P6 - Top Auxiliary Plug.STL
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

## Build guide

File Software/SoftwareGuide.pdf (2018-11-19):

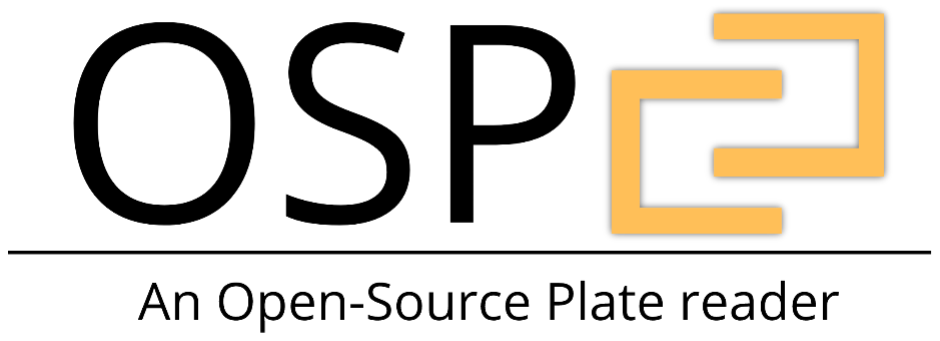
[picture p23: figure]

# SOFTWARE USER GUIDE

## Contents

Getting Started | S1
Requirements | S1
Installation | S1
Windows/Mac | S1
Raspberry-Pi | S3
Repository Structure Guide | S4
Hardware | S4
Software | S4
Before Running a Protocol | S5
Initial Function Testing | S5
Testing Light Sources | S5
Testing Linear Actuators | S5
Calibration Guide | S6
Loading a Plate | S6
Software Structure | S7
Structure Overview | S7
Structure Guide | S8
System.py | S8
GUI.py | S9
PlateConfiguration.py | S10
Protocol.py | S10
Absorbance.py | S11
Fluorescence.py | S11
Auxiliary.py | S12
Shake.py | S12
Kinetic.py | S12
Machine.py | S13
Arduino.py | S13
Spec.py | S14
System Level Control | S14
GUI Level Control | S15
Running the GUI | S15

The Intro Screen | S15
The Settings Screen | S16
The Plate/Well Selection | S17
The Protocol Selection | S18
Kinetic Toggling | S19
Absorbance Settings | S20
Fluorescence Settings | S20
Auxiliary Settings | S21
Review Protocol Sequence | S22

Return to Table of Contents | S1

## Getting Started

### Requirements

The OSP software is written in Python 2.7 and utilizes the PyQt4 package to create a functional user interface. Below is a list of all the python packages required to successfully use the OSP device.

- PyQt 4
- Seabreeze
- Numpy
- Pickle
- Platform
- Xlsxwriter
- Matplotlib
- Time
- Serial
- Warnings

In addition, the Arduino IDE will have to be installed in order to load the OSP Arduino script (provided in this repository) on the device’s Arduino UNO board.

The installation section below will guide you through installing all python packages and any programs required.

### Installation

Windows/Mac

Installation of OSP software requirements on any Windows/Mac device is accomplished utilizing Anaconda, which should come prepackaged with all requirements except PyQt4, Seabreeze, Pyserial and Git. The following instructions require you to write in command line. If you have never used command line visit the following LINK (Windows) or LINK (Mac) for a quick intro.

Step 1. Install Anaconda – Visit the following LINK to download the Anaconda software. Be sure to download the version for Python 2.X and your specific OS environment (Windows/Mac). When prompted whether to add Anaconda to your path select yes.
Step 2. Install Git– Visit the following LINK to download the Git software. When prompted whether to add Git to your path select yes.

Step 3. Clone the OSP repository – Open the Terminal on your computer as an administrator. To do this, find the Terminal application, right-click it and select Run as administrator. To clone the repository onto your system, type the following lines of code (Make sure to use the ones specific to your OS):

Windows

cd %USERPROFILE%
git clone https://github.com/brianchowlab/OSP.git

MAC

cd ~
git clone https://github.com/brianchowlab/OSP.git
Step 4. Run the OSP installation script – In the open Terminal window type the following lines of code and leave the window open:

Windows

.\OSP\Software\install_pc_reqs.sh

MAC

./OSP/Software/install_pc_reqs.sh

Step 5. Install Arduino IDE – Visit the following LINK to download the latest Arduino IDE.
Step 6. Upload OSP script to Arduino UNO – Using the Arduino IDE, open up the OSP Arduino script located in the cloned repository folder OSP\Software\Arduino Files\OSP_Serial_Communication. Make sure the Arduino is plugged into the USB hub in the OSP device and that the OSP device is connected to your computer via USB. Click the UPLOAD button in the Arduino IDE to compile and upload the code to the Arduino UNO.
Step 7. (ONLY WINDOWS USERS) Setting up Seabreeze Drivers – Visit the following LINK and click the download button. Extract the .zip file to a known location. Open Device Manager on your Windows machine. Connect your computer to the OSP device via USB. In the Device Manager’s list of devices make sure that there is now a tab named Ocean Optics USB Devices. In that tab, there should be a device named Ocean Optics STS (WinUSB). If this device is present you can now move on to step 9.

If for some reason, you cannot find Ocean Optics USB Devices in the Device Manager you will have to manually set-up the drivers. To do this, in the Device Manager find the tab labeled Other Devices. In that tab there should be a device named STS. Right-click on this device name and select Update drivers from the drop-down menu. Next, a window will pop up asking you where the system should look for the drivers. Select the Browse my computer for the driver software option. On the next screen click the browse button and direct the system to the windows-driver-files folder which you downloaded & extracted at the beginning of this step.

Step 8. Opening the user interface – In order to start utilizing the OSP device, make sure the device is turned on and plugged into the computer via USB. In your open Terminal type the following lines of code:

Windows

activate osp
cd “OSP\Software\Python Files” python GUI.py

MAC

source activate osp
cd “OSP/Software/Python Files” python GUI.py

Raspberry-Pi

The simplest way to install the OSP software on a Raspberry-Pi is downloading and installing the OSP.img file provided. In order to do this, you will need to have a completely empty 16GB Micro SD Card. If the card is not empty, all of its contents will be deleted in the installation of the OSP.img file. In addition, the first 3 installation steps need to be performed on a computer/laptop with an SD card slot.

Step 1. Download & Unzip the OSP.img – Visit the following LINK and click the DISK IMAGE FILE link and download button. Once downloaded, unzip the file to a known location.
Step 2. Download & Install the Etcher program – Visit the following LINK and download the Etcher program for your specific operating system.
Step 3. Install the OSP.img onto the SD card – Insert your empty SD card into the computer. Start up the Etcher software and follow the on-screen instructions in order to install the OSP.img onto the card. This process can take up to 10 minutes.
Step 4. Update the OSP repository – Once the OSP.img file is installed, insert it into your Raspberry-Pi (which should be connected to the turned on OSP device, touch-screen/monitor, keyboard & mouse). Turn the Raspberry-Pi on and when it is booted open the Terminal. Type the following and close the window when it is finished:

cd OSP
git pull origin master

Step 5. Running the User Interface – To activate the user interface, make sure the OSP device is turned on and connected to the Raspberry-Pi via USB. Open up the Terminal and type the following:

cd “OSP/Software/Python Files”
sudo python GUI.py

### Repository Structure Guide

Below you will find a detailed explanation of how the repository is structured, including folder and file descriptions.

Hardware
All the files required for assembly of the OSP device are in this folder. The full Assembly Guide and Parts List can be found here as a PDFs.

CAD Files
All files necessary to 3D-print custom parts for the OSP device are found here. Each part is labeled according to its part number in the Parts List

Laser-Cut Files
All files necessary to laser-cut custom parts for the OSP device are found here. Each part is labeled according to its part number in the Parts List

PCB Files
All files necessary to order custom-made PCB board for the OSP device are found here. Each part is labeled according to its part number in the Parts List.

Software
All the files for installation and execution of the OSP software are in this folder. The full Software Guide can be found here as a PDF.

Arduino Files
The main Arduino script is found in this folder.

Graphical Designer Files
All raw GUI Designer files are found in this folder. GUI graphics are derived from these files.

Python Files
Data
This directory is where all saved data from experiments are saved in the form of .xlsx files.

Images
This directory contains all the image files referenced in the GUI.

Protocols
This directory is where all protocol sequences are saved from the GUI

Screens
This directory contains the Python equivalent of the graphical files found in Software/Graphical Files

System Settings
This directory contains the setting files such as calibrated well positions, excitation LED wavelengths, and the number of scans to average during a measurement.

All Other Files
These rest of the files are Python scripts containing the class objects from which the GUI is accessed. An explanation of each of these classes is provided in the next section.

## Before Running a Protocol

### Initial Function Testing

Once the OSP device is fully built and connected to a computer or Raspberry-Pi, it is useful to test the functionality of the linear actuators and light sources. To do so, open up the Arduino IDE, click on the Tool tab in the menu bar, and select the Serial Monitor from the drop-down menu. Follow the instructions below and enter the commands to test the functionality of individual components:

Testing Light Sources
To test LED 1 type: L1;
This should result in the LED 1 turning on. To turn it off, type the same command in again.

To test LED 2 type: L2;
This should result in the LED 2 turning on. To turn it off, type the same command in again.

To test LED 3 type: L3;
This should result in the LED 3 turning on. To turn it off, type the same command in again.

To test LED 4 type: L4;
This should result in the LED 4 turning on. To turn it off, type the same command in again.

To test LED 5 type: L5;
This should result in LED 5 & LED 6 turning on. To turn them off, type the same command in again.

Testing Linear Actuators
To extend Linear Actuators type: M1500.001500.00;
This should result in both linear actuators extending to about half their limit.

To contract the linear actuators type: M1000.001000.00;
This should result in both linear actuators fully contracting.

### Calibration Guide

The software provided in this repository comes with pre-loaded calibrated positions for a 24-well plate and a 96-well plate. However, it is recommended that an initial calibration is performed after the OSP device is built to account for any small difference

Before performing any sort of calibration, you will need to prepare the calibration lid for the specific plate-type that is to be calibrated. Refer to the Calibration Lid Assembly at the end of the General Assembly Guide for instructions on how to do this.

The following steps should be followed every time a calibration is performed:

Step 1. Attach fiber to photodiode – Detach the fiber from the STS spectrophotometer and screw it into the photodiode mount.
Step 2. Adjust the iris size – As part of the Top Optics Assembly there is an iris. Using the markings on the rim of the iris, set the size of it to 2.
Step 3. Insert plate into OSP device – Place the calibration lid onto an empty micro-well plate and insert it into the device (refer to the next section about proper orientation).
Step 4. Initialize calibration – On the GUI press the Calibrate button and when prompted input the size of the micro-well plate (24 or 96). The machine will begin the calibration process and alert you when it is finished. This process takes around 3 minutes.

### Loading a Plate

The orientation in which you load the plate is important not only for the calibration process but also for any sort of measurement performed on the OSP device. Please refer to the below picture to ensure you are loading the plate correctly. The plate should be held firmly in place with the attached springs.

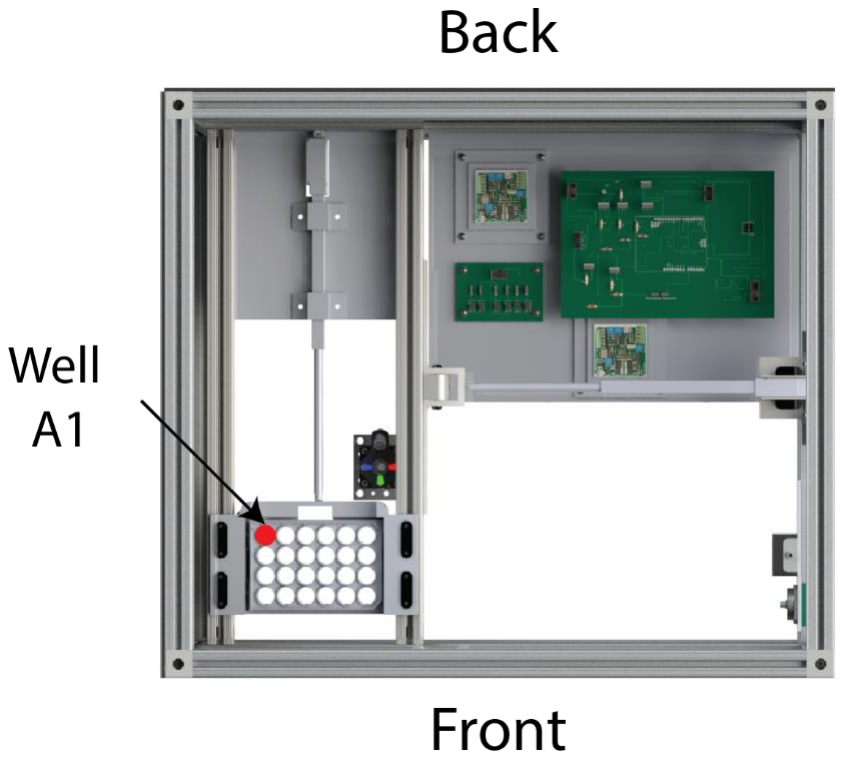
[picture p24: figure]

## Software Structure

The OSP software is object oriented and composed of a total of twelve class objects. The below sections will explain the structure of the software and how information is passed between the objects.

### Structure Overview

The diagram below depicts the general flow of information between the 6 main software objects. The entire structure can be divided into three separate categories based on functionality.

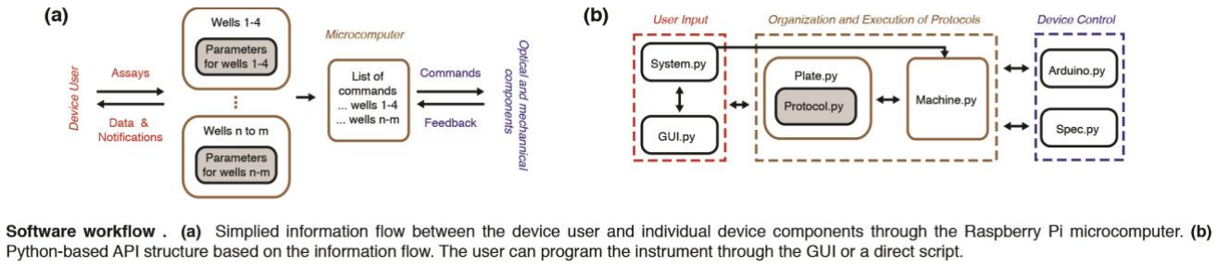
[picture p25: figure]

System.py and GUI.py are the primary classes that allow the user to interface with the plate reader. They track and store user input. System.py is the object that contains all the vital functionality of translating the user input into commands to change device settings. This object is responsible for loading-in user settings (such as calibrated well coordinates and excitation led wavelengths) and for preparing the system for execution of input protocols. The user can call this object to set-up and execute protocol sequences from a Python script (more information about this and examples in System Level Control). Alternatively, the user can control the device via the provided GUI (GUI.py) object. The GUI.py object (the visual user interface) has access to all the functions and variables of the System.py object.

User input (into either the GUI.py or System.py constructs) results in the creation of a PlateConfiguration.py object containing a list of Protocol.py objects. This combination of classes organizes the desired sequence of protocols to be executed. The PlateConfiguration.py object contains a list of the selected wells and a separate list of the protocols to be run. As mentioned before, the list of protocols is a list of protocol objects (e.g. Absorbance.py is an object for an absorbance protocol and it inherits its attributes from the Protocol.py object). Each protocol object contains all the necessary parameters (spectrophotometer settings, excitation LED, acquisition type, etc.) for it to be executed.

The user is not limited to one PlateConfiguration.py structure. Performing separate protocols on different sets of wells would simply require multiple PlateConfiguration.py objects to be created. For example, to measure fluorescence from the set of wells [A1, A2, A3] using a 470nm LED and then measure fluorescence from the set of wells [D1, D2, D3] using a 610nm LED, the system would create two PlateConfiguration.py objects (one for each set of selected wells); the first PlateConfiguration.py object would represent the set of wells [A1, A2, A3] and contains a single Fluorescence.py object (for the scan with 470nm excitation), and the second PlateConfiguration.py object would represent the set of wells [D1, D2, D3] and also contains a single Fluorescence.py object (for the scan with 610nm excitation).

Once the PlateConfiguration.py object(s) is/are created, a list of these objects is sent to the Machine.py construct. This object is the control center of the entire software. Machine.py is responsible for parsing through the list of PlateConfiguration.py objects and their respective Protocol.py objects. As it parses these protocols, it sends the respective commands to the Arduino.py and Spec.py structures to perform the necessary operations to successfully execute the inputs. In other words, Machine.py is the object responsible for sending commands to the Arduino to tell it to move the linear actuators or to turn on/off the LEDs or external devices (except for the detector). In addition, it extracts spectra from the spectrophotometer and outputs the extracted data to a properly formatted Excel sheet. As a result, there is constant bi-directional communication between the Machine.py, Arduino.py & Spec.py objects.

A more detailed description of the functions and attributes of the involved class objects are below.

### Structure Guide

This section describes each Python object and the functions which are available to call from it. For syntax details and examples of usage please refer to the System Level Control section as well as the commented source code.

System.py
Description:
This class object’s main purpose is to track user inputs and adjust the system wide settings accordingly. It contains all the necessary functions to add plate objects to the protocol sequence, load calibration data, add protocols, and retrieve information about existing protocols.

Functions:
load_calibration_data() – Used to load calibrated well-position data into system. load_settings() – Used to load the system settings from the settings file. This includes the labeled wavelengths of the excitation LEDs. save_settings() – Used to save system settings to the settings file.
load_well_labels() – Used to make a list of well labels when the object is made. set_plate_type() – Creates a new plate object and sets it as either 24 or 96 well. set_current_plate() – Used to select a plate object so that it can be edited. get_current_plate_type() – Returns whether the current plate is 24 or 96 well. get_plate_count() – Returns the total number of plate objects.
remove_plate_object() – Removes the plate object.
get_selected_wells() – Returns the labels of the selected wells for a specific plate object. get_settings() – Returns a list containing the system settings.
select_wells() – Select a specified set of wells for a specific plate object.
clear_wells() – Unselect any selected wells from a specific plate object. select_all_wells() – Select all wells for a specific plate object. add_absorbance_protocol() – Add an absorbance protocol to a specific plate object. add_fluorescence_protocol() – Add a fluorescence protocol to a specific plate object. add_auxiliary_protocol() – Add an auxiliary protocol to a specific plate object. turn_kinetic_tracking_on() – Used to mark the start of a kinetic cycle.

add_kinetic_absorbance_protocol() – Used to add an absorbance protocol to a kinetic cycle. add_kinetic_fluorescence_protocol() – Used to add a fluorescence protocol to a kinetic cycle. add_kinetic_auxiliary_protocol() – Used to add an auxiliary protocol to a kinetic cycle. get_all_protocol_brief_descriptions() – Returns brief descriptions (Labels & Index) of all protocols in a plate object. get_all_protocol_full_description() – Returns detailed descriptions (Labels & Settings) of all protocol in a plate object. initialize_machine() – Opens an instance of the Machine object.
initialize_datasheet() - Creates the data output file.
start_program() – Executes the protocol sequence. close_machine() – Closes the instance of the Machine object.

GUI.py
Description:
This object contains all the code that comes together to create the User Interface. Running this object will bring up an instance of the GUI. For details about how to use the interface see the GUI Level Control section. This class object has access to all the functions that are in System.py.

Functions:
move_plate_out() – Moves plate holder into position by the front door panel. initialize_calibration() – Runs the calibration sequence
change_settings() – Used to change system settings such as excitation LED wavelengths. update_settings() – Used to update the system settings file.
start_plate_selection() – Opens the plate selection screen of the GUI start_well_selection() – Opens the well selection screen of the GUI start_protocol_selection() – Opens the protocol selection menu of the GUI load_protocol_sequence() – Loads in a saved protocol sequence from a file. save_protocol_sequence() – Used to save the currently selected protocol sequence to a file. add_new_plate_configuration() – Adds a new plate object and brings up well selection menu. back_function() – Used to return to previous screen.
open_protocol() – Opens the menu for a selected protocol.
add_protocol() – Adds the protocol and its settings to the protocol sequence. review_protocols() – Brings up the review screen of the GUI
initialize_program() – Starts the execution of the protocol sequence
reset_system() – Resets system. Clears the protocol sequence and returns to main menu. add_items() – Function to add object to the QTreeWidget (PyQt)
get_current_item() - Function to get selected object from the QTreeWidget (PyQt) remove_plate() – Deletes a plate object and all its protocols from the protocol sequence. remove_protocol_selection() – Deletes a protocol object from the protocol sequence. edit_protocol_selection() – Brings up the menu of the chosen protocol and allows editing. update_protocol() – Sets the edits made to a protocol and updates the protocol sequence edit_knetic_protocol_selection() – Used to edit a protocol part of a kinetic cycle update_kinetic_protocol() - Sets into place the edits made to a protocol that is a part of a kinetic cycle and updates the protocol sequence. add_parent() – Function to add object to the QTreeWidget (PyQt)

add_child() – Function to add object to the QTreeWidget (PyQt) add_subchild() – Function to add object to the QTreeWidget (PyQt)

PlateConfiguration.py
Description:
This object contains all the information about a specific plate configuration input by the user. A plate configuration is defined as a set of wells to run specific protocols on. Each plate object contains the following information:
(1) The plate type (24 or 96)
(2) List of protocol of objects (the protocol sequence to perform on the selected wells)
(3) List of selected wells.
(4) Overall ordering if there is more than one plate configuration input by the user.

Functions:
add_protocol() – Used to add a protocol object to the list of protocols. get_protocol_count() – Returns the current number of protocols in the protocol list initialize_wells() – Creates a list of well labels when the plate object is created. get_protocol_brief_description() – Get a short description of the specified protocol. get_protocol_full_description() – Get a detailed description of the specified protocol. remove_protocol() – Removes a protocol from the protocol list. get_selected_wells() – Returns the labels of the wells selected for the plate object. get_well_status() – Returns list describing whether a well is selected or not. clear_wells() – Used to unselect all wells.
selected_all_wells() – Used to select all wells.
select_wells() – Used to select a specified set of wells.

Protocol.py
Description:
This object is a general parent class for all possible protocols. It contains the following general information about the selected protocol:
(1) The protocol label (Absorbance, Fluorescence, Auxiliary, or Kinetic)
(2) The plate index to which the protocol is assigned to
(3) The order number of the protocol in the protocol list of the assigned plate object.

Functions:
get_brief_description() – Returns a short description (Label & Index in protocol list) of the protocol

Absorbance.py
Description:
This object contains all the system settings and necessary information to perform an absorbance measurement with settings defined by the user:
(1) The exposure time.
(2) The list of steps that need be run by the machine to perform the measurement.
(3) The excel sheet layout of the measurement results.

Functions:
get_full_description() – Returns detailed description (Label & Setting Information) of protocol get_exposure_time() – Returns exposure time of protocol
set_exposure_time() – Sets the exposure time of protocol
initialize_excel_section() – Creates the header of the protocol in the data output file. get_dark() – Includes list of Machine.py commands to execute to perform a dark measurement.
start() – Includes list of Machine.py commands to execute to perform an Absorbance measurement.

Fluorescence.py
Description:
This object contains all the system settings and necessary information to perform a fluorescence measurement with settings defined by the user:
(1) The exposure time.
(2) The list of excitation LEDs to trigger.
(3) The list of steps that need be run by the machine to perform the measurement.
(4) The excel sheet layout of the measurement results.

Functions:
get_full_description() - Returns detailed description (Label & Setting Information) of protocol get_exposure_time() - Returns exposure time of protocol
get_led_index() – Returns a string describing which excitation LED(s) were chosen get_wavelength() – Returns the wavelength(s) of the selected LED(s)
set_exposure_time() – Sets the exposure time of the protocol set_excitation_source() – Sets which excitation LED(s) will be used. initialize_excel_section() - Creates the header of the protocol in the data output file. get_dark() – Includes list of Machine.py commands to execute to perform a dark measurement.
start() – Includes list of Machine.py commands to execute to perform a Fluorescence measurement.

Auxiliary.py
Description:
This object contains all the system settings and necessary information to perform a measurement using the auxiliary port with settings defined by the user:
(1) The exposure time.
(2) The list of auxiliary ports to trigger.
(3) The list of steps that need be run by the machine to perform the measurement.
(4) The excel sheet layout of the measurement results.

Functions:
get_full_description() - Returns detailed description (Label & Setting Information) of protocol get_duration() – Returns the duration in milliseconds
get_aux_index() – Returns which auxiliary port is being used.
set_duration() – Used to set the duration in milliseconds.
start() - Includes list of Machine.py commands to execute Auxiliary functionality.

Shake.py
Description:
This object contains all the system settings and necessary information to initialize and perform shaking of the plate:
(1) The list of steps that need be run by the machine to perform the measurement.

Functions:
get_full_description() - Returns detailed description (Label & Setting Information) of protocol start() - Includes list of Machine.py commands to execute Auxiliary functionality.

Kinetic.py
Description:
This object is for time-course measurements. This object represents a set of protocols which need to be performed on each individual well. The following information is contained within this object:
(1) The order number of the object in the list of protocols of the assigned plate configuration
(2) The type of kinetic method: Interval (regular interval over specified time) or Repeat (repeated set number of time)
(3) List of protocol of objects (the protocol sequence to perform in the Kinetic cycle)
(4) The layout of the excel sheet of the results of the kinetic cycle

Functions:
get_full_description() - Returns detailed description (Label & Setting Information) of protocol add_protocol() - Add protocol to the Kinetic cycle.
remove_protocol() – Remove protocol from kinetic cycle.
get_protocol_count() - Returns the current number of protocols in the kinetic cycle. get_protocol_brief_description() - Returns a short description (Label & Index in kinetic cycle) of the selected protocol.

get_protocol_full_description() - Returns a detailed description (Label & Setting information) of the selected protocol.
get_protocol() – Returns the selected protocol object.
initialize_excel_section_start() - Creates the header of the protocol in the data output file that represents the start of the kinetic cycle. initialize_excel_section_stop() - Creates the header of the protocol in the data output file that represents the stop of the kinetic cycle.

Machine.py
Description:
This object contains all the functions to interface with the Arduino, Ocean Optics spectrophotometer, and Excel sheet to which the resulting data is being written to. Each protocol object contains a list of commands that the machine object needs to perform in order to execute the specific protocol.

Functions:
Initialize_arduino() – Creates an Arduino object and begins Serial communication. initialize_spec() – Creates a Spec object.
move_plate() – Used to move plate to specific position.
turn_led_on() – Used to turn LED on
turn_led_off() – Used to turn LED off
trigger_aux() – Used to trigger an auxiliary port.
set_exposure_time() – Used to set the exposure time of the spec. set_scans_to_avg() – Used to set the number of scans to average on the spec. set_boxcar_width() – Used to set the boxcar width of the spec.
calibrate() – Used to run the calibration sequence
start_program() – Used to start protocol sequence execution.

Arduino.py
Description:
This object is used to interface with the Arduino. It allows the user to write and read to and from the Arduino’s Serial.

Functions
write() – Used to write to the Serial port of the Arduino.
read() – Used to read from the Serial port of the Arduino. close() – Disconnects system from Arduino.

Spec.py
Description:
This object is used to interface with the Ocean Optics Spectrophotometer through their API. It allows the user to set exposure time, boxcar width, scans to average, and to capture spectra.

Functions
For functions, see the linked Seabreeze documentation.

## System Level Control

System level control of the OSP device refers to setting up and executing protocols via a manual Python script. An example script which shows the basics of how to write a Python script to execute OSP protocols is provided in the Python Files directory of the repository and can be opened with any text editor. Refer to the comments in the script for details about functions and their use. The script can also be run by typing the following lines of code in the terminal:

Windows

activate osp
cd %HOMEPROFILE%
cd “OSP\Software\Python Files” python system_ex1.py

MAC

source activate osp
cd ~
cd “OSP/Software/Python Files” python system_ex1.py

1

2

3

4

## GUI Level Control

### Running the GUI

If working from a Raspberry-Pi, the best way to initialize OSP is to use the Terminal, direct the Pi to the ‘Python Files’ directory, and run GUI.py from there. If not running on a Raspberry-Pi, simply run GUI.py either from the Terminal (refer to the Running the User Interface steps in the Installation section).

!!! Important Note !!!: The size of the GUI has been optimized for the Raspberry-Pi Touch Screen. If you have a high-resolution display (e.g. 4K), you may need to adjust resolution to display the GUI properly (recommended 1280x720). Users with standard resolution displays (e.g. 1920x1080) should be fine with their default settings and should not have to change the resolution.

### The Intro Screen

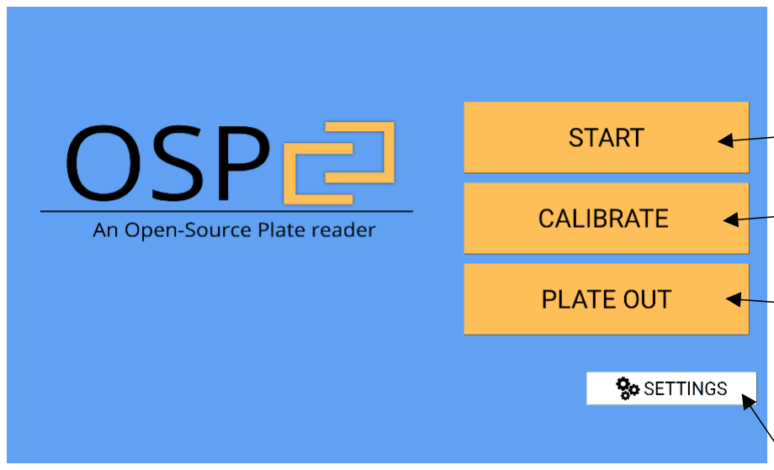
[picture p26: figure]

1. The START button leads to the plate selection screen, where the user can input whether they will be using a 24-well plate or a 96-well plate for the protocol sequence.
2. The CALIBRATE button allows the user to re-calibrate the well positions in the system for either a 24-well plate or a 96-well plate. When pressed, a pop-up message shows up asking the user to input the plate-type (24 or 96) that they wish to calibrate the positions for.
3. The PLATE OUT button allows the user to have the device move the plate holder to the edge of the front door for plate loading and removal.
4. The SETTINGS button brings the user to the Settings Window, where they are allowed to change specific settings of the system.

1

2

### The Settings Screen

Here, the user has access to change the system settings, specifically, the LED wavelength labels and the number of scans to average.

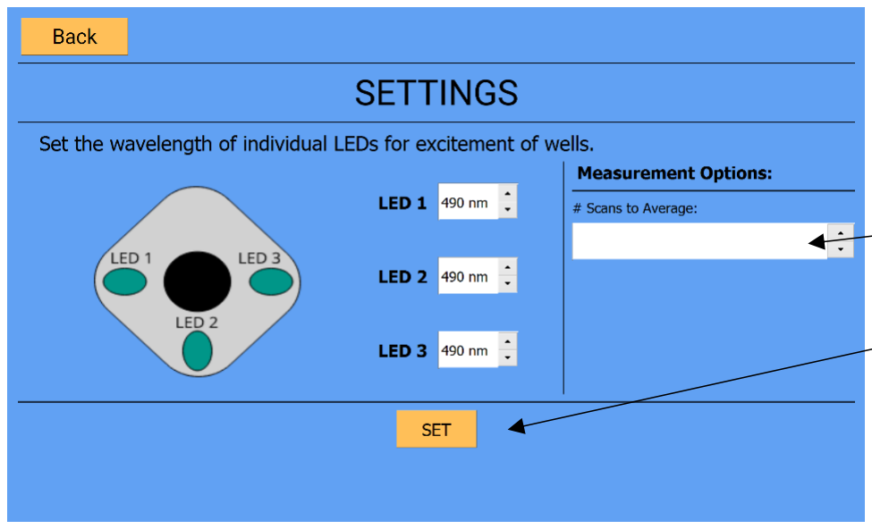
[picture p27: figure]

1. Here, the user can enter an integer to change the number of scans that the spectrophotometer averages when performing a measurement.
2. The three LEDs correspond to the three excitation light sources. Here the user can change the wavelengths to describe the LEDs connected to a specific LED socket position (or digital switch). These wavelengths are then used as reference for data output.

### 3. Once the user clicks the SET button the displayed settings are saved to ‘…/System

Settings/savedSettings.txt’.
4. Hitting the BACK button will take the user to the home screen or the protocol selection screen (depending on which screen was up/active before the settings were accessed).

### The Plate/Well Selection

The user has the option to select which type of plate they will perform the protocol sequence on. A protocol sequence can only be run on one type of plate. Plate selection leads the user to the well selection window for the chosen plate type.

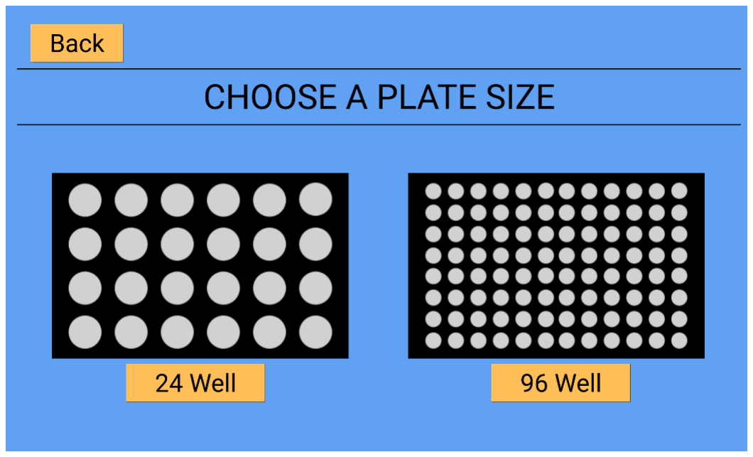
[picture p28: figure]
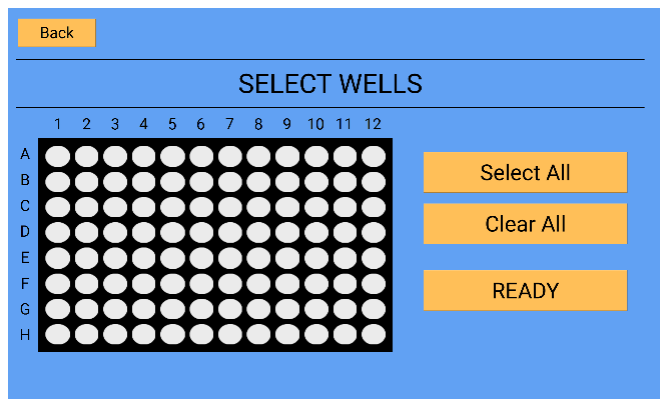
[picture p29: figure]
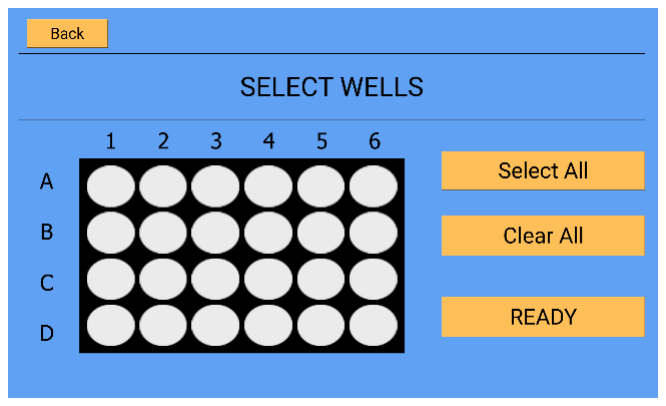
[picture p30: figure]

Click & Drag to select wells. Pressing the ‘BACK’ button will return the user to the plate selection window.

1

2

9

### The Protocol Selection

From this screen, the user can choose to add specific protocols to their protocol sequence. Settings may also be changed from this screen.

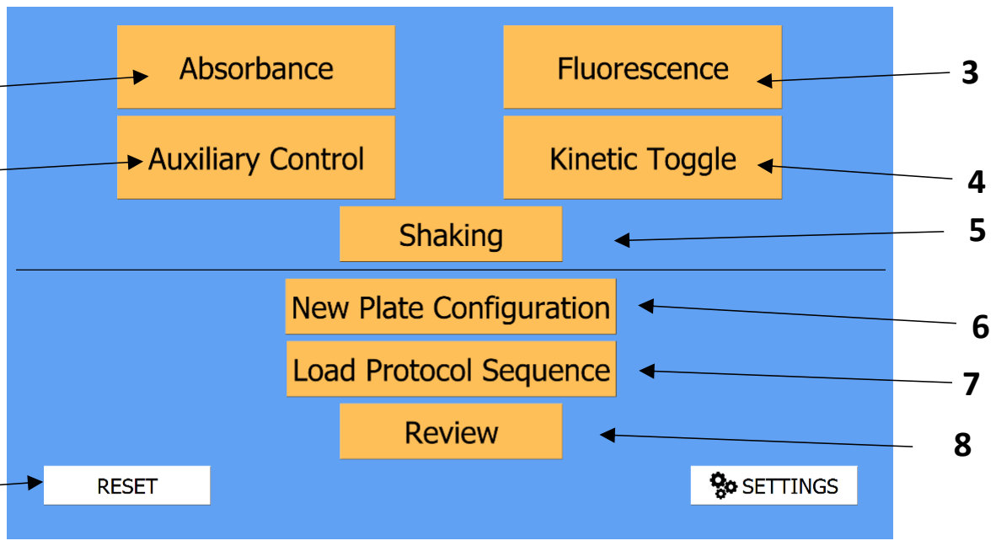
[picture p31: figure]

1. The ABSORBANCE button takes the user to the absorbance protocol settings screen. This allows the user to set the exposure time.
2. The AUXILIARY CONTROL button takes the user to the auxiliary control settings screen. Here, the user can choose which auxiliary port to turn on and for how long.
3. The FLUORESCENCE button takes the user to the fluorescence protocol settings screen. Here the user chooses which excitation LED to use and sets the exposure time of the measurement.
4. The KINETIC TOGGLE switch allows the user to turn on/off a kinetic cycle (time-course).
5. The SHAKE button adds a protocol to shake the plate for 5 seconds.
6. The NEW PLATE CONFIGURATION button allows the user to create a new selection of wells for a different protocol sequence. Going down this path creates a new PlateConfiguration.py object.

### 7. The LOAD PROTOCOL SEQUENCE button allows the user to load a pre-existing (custom made)

protocol sequence that has been saved to the repository. The loaded sequence will replace the current protocol sequence.
8. The REVIEW button takes the user to the review screen where they can see the protocol sequence resulting from their inputs, and edit any of the protocols individually or remove them.
9. The RESET button will take the user back to the main screen and clear the system of any protocols and well selections.

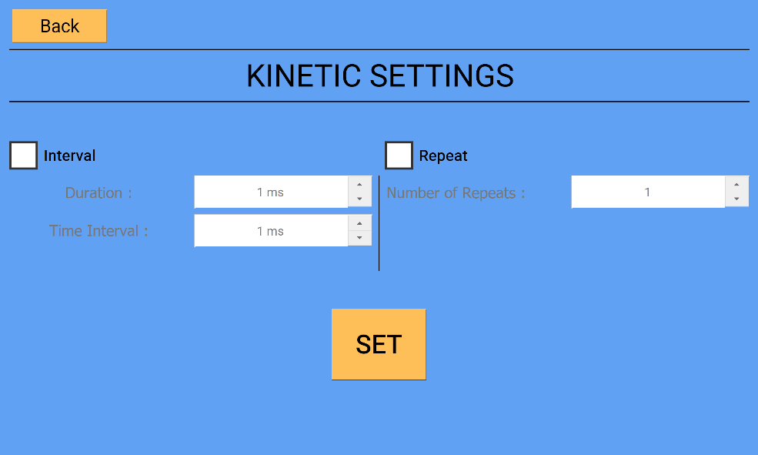
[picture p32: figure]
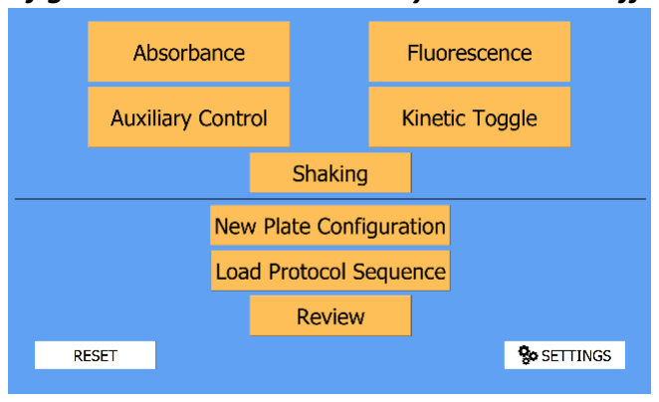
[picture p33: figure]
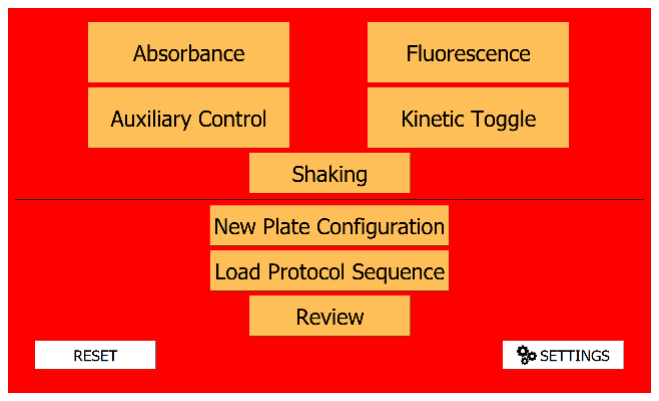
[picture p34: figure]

Kinetics OFF | Kinetics ON

### Kinetic Toggling

“Kinetics” allows the user to iteratively perform a specific protocol for time-course measurements without having to manually repeat the inputs. OSP allows two methods of kinetics: (1) Interval and (2) Repeat. Note that the user can only select one method, described below:

Interval Kinetics:
This method performs a protocol or a sequence of protocols in intervals (based on the interval specified by the user) for a specific duration (e.g. absorbance of a sample every 10 seconds for 2 minutes). The user must ensure that the time it takes to perform the specific protocol or sequence of protocols does not exceed the interval time.

Repeat Kinetics:
This method simply repeats a protocol or a sequence of protocols the specified number of times. Once the SET button is pressed on the ‘Kinetic Settings’ screen, the user is taken back to the protocol selection menu, which will then have a background that is bright red. The kinetic state is set to ON as long as the background is red. To toggle the kinetic cycle off, press the kinetic button again and the screen will return to its original (blue) color. The user will not be able to review the protocol or add a new plate configuration until the kinetic cycle is turned off.

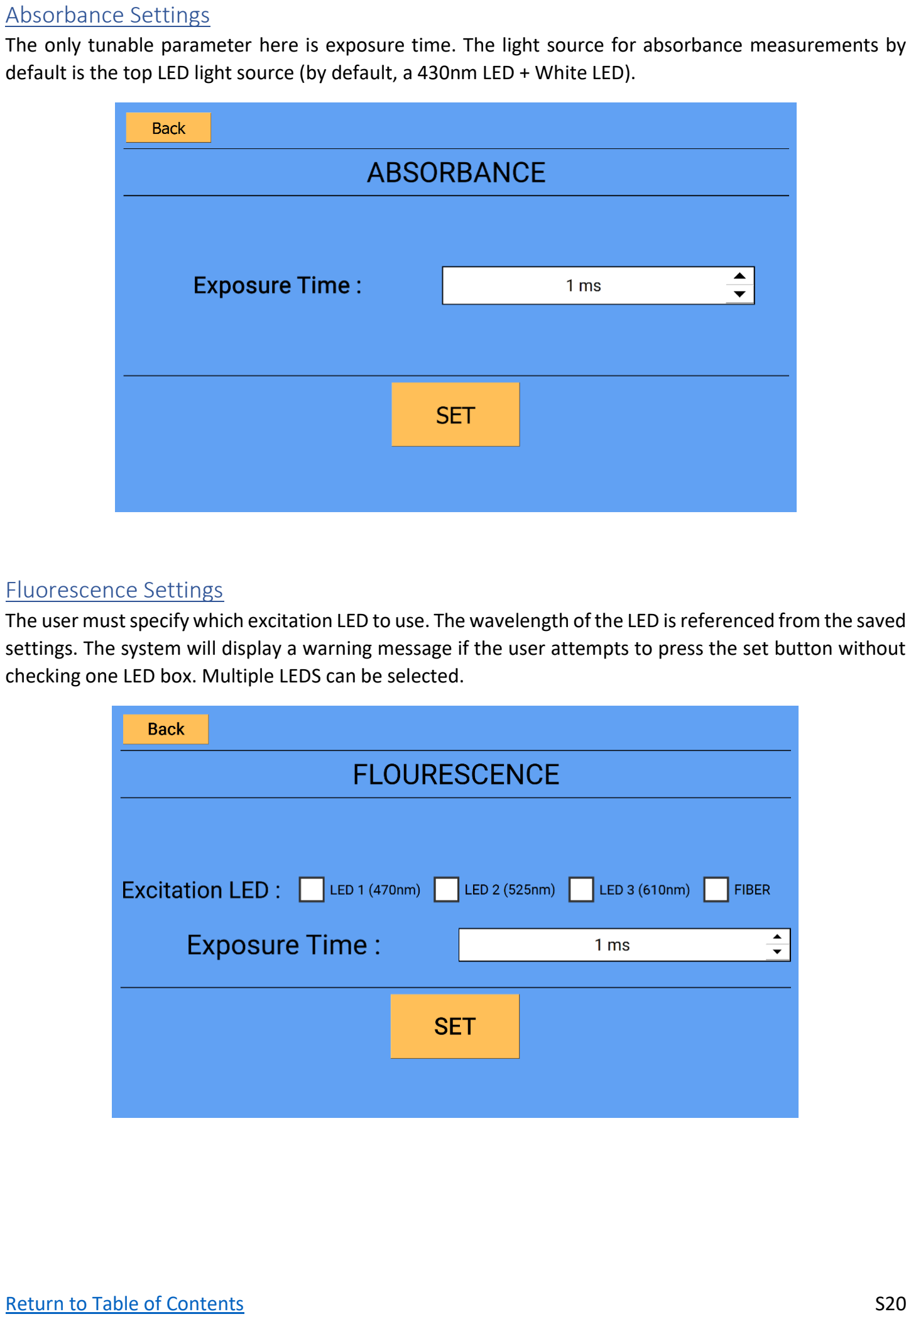
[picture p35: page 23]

### Absorbance Settings

The only tunable parameter here is exposure time. The light source for absorbance measurements by default is the top LED light source (by default, a 430nm LED + White LED).

### Fluorescence Settings

The user must specify which excitation LED to use. The wavelength of the LED is referenced from the saved settings. The system will display a warning message if the user attempts to press the set button without checking one LED box. Multiple LEDS can be selected.

### Auxiliary Settings

Here, the user can select which auxiliary port (see “Top Optical Train” Assembly) they want to turn on by digital logic, and for what duration of time. Note that only one port can be turned on at one time. One port is specifically for unpowered LEDs. The other three communication ports are more customizable; to access their trigger ports, see the DB9 port pin-out diagram on the next page. By default, triggering a port also moves the motors to position the selected well under the top auxiliary optics attachment.

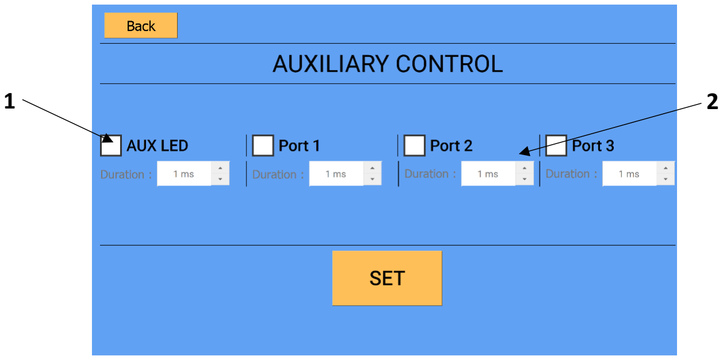
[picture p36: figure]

1. The AUX LED PORT (LED #4) controls an extra unpowered LED of choice, and the default limiting resistor sets the current to ~20mA (assuming a ~3V LED bias voltage). Setting the ‘duration’ sets the amount of time this auxiliary LED is on once the well is positioned under it.
2. Any of the three generic ‘ports’ allows direct control of external electrical connections that can be accessed through the DB9 header (see below diagram for pin-out). Each port contains two data pins (1 IN and 1 OUT) for digital control and inputs to/from the Arduino. The user can customize an Arduino script for automating external devices. For custom series of events where movement under the auxiliary piece is not required, this default can be eliminated by commenting out the movement function (machine.move_plate()) for the corresponding port number of the Auxiliary.py script.

When accessing the auxiliary port +12V power (pin 3), the total current draw should be less than 3 amps to ensure sufficient power for all internal components. When accessing the auxiliary port +5V power (pin 3), the total current draw should be less than 1.5 amps to prevent damage to the internal switch.

1. +5V
2. Port 2: Trigger
3. +12V
4. GND
5. Port 1: Data In
6. Port 1: Trigger
7. Port 2: Data In
8. Port 3: Trigger
9. Port 3: Data In

1

2

3
4

### Review Protocol Sequence

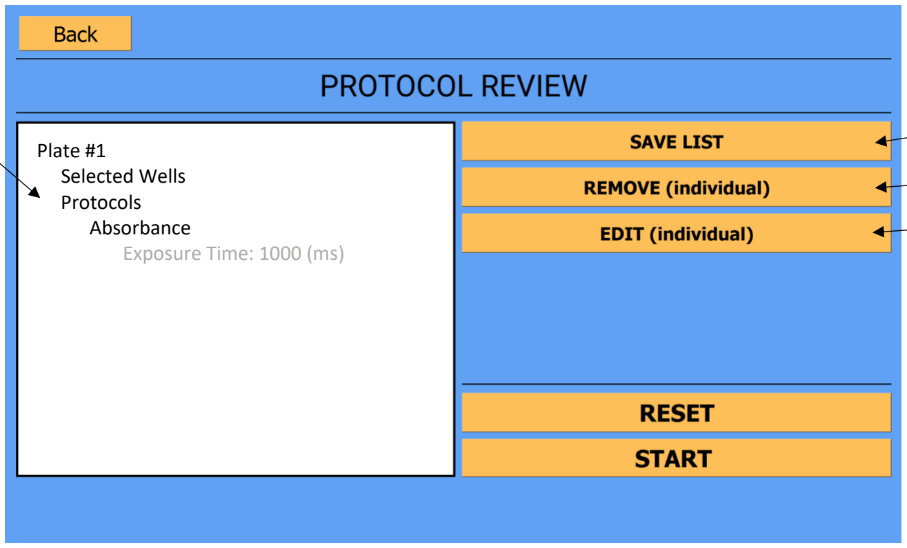
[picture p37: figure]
Plate #1 Selected Wells Protocols Absorbance Exposure Time: 1000 (ms)

1. Window displaying the selected plates & protocols in their desired order. Each selection in the window is selectable. By highlighting one of the protocols, the user can edit/remove it.
2. The SAVE LIST button allows the user to save the current set of protocols in their order as a ‘protocol’ object. NOTE: When saving a sequence of protocols, the system saves the protocols and all their settings in shown order, and the plate type. The loaded sequence plate type cannot be changed unless the system is reset.

### 3. The REMOVE button allows the user to remove one of the protocols OR an entire plate

configuration from the protocol sequence. If a plate configuration (e.g. Plate #1) is selected, that entire plate object and all of its assigned protocols will be deleted. NOTE: The user can only delete one protocol or plate at a time.
4. The EDIT button allows the user to edit a single protocol or a single selection of wells. In order to edit the selected wells, the user needs to highlight the selected wells tab.

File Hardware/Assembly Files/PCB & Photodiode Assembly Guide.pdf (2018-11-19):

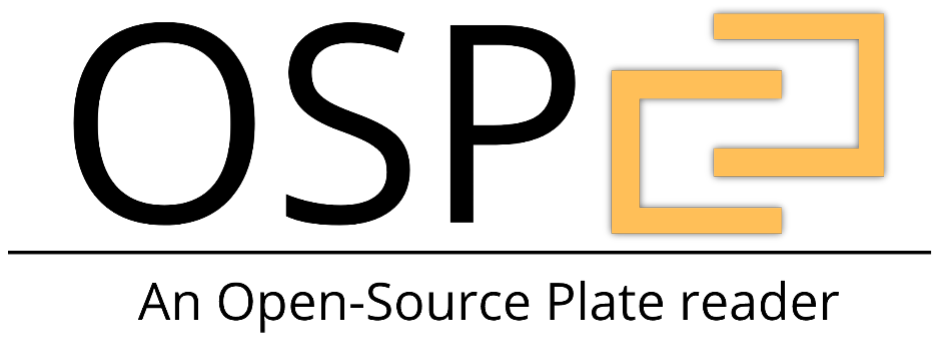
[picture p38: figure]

# PCB AND PHOTODIODE ASSEMBLY GUIDE

# Main Power Board

Numbers refer to Parts List numbering

1. Solder all resistors to their respective places (red dashed circles). Resistor values are printed on the boards. There are 11 resistors total.

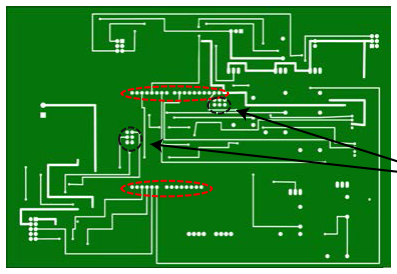
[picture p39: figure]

2. Flip the board over. Solder all standard male headers (#E21) into their positions (red dashed circles). Solder all standard female headers
(#E22) | into | their positions (black dashed
circles). There are two headers each.

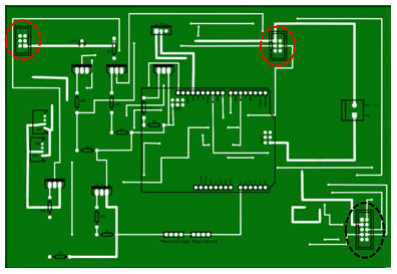
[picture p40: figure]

3. Flip the board right-side. Solder the 2x3 IDC headers (#E17) to their positions (red dashed circles), with the orientation of the tab on the header matching the PCB silkscreen. There are two headers.
4. Solder the 2x5 IDX header (#E18) to its position (black dashed cirlce), with the orientation of the tab on the header matching the PCB silkscreen. There is one header.

Female Headers (#E22)

S1

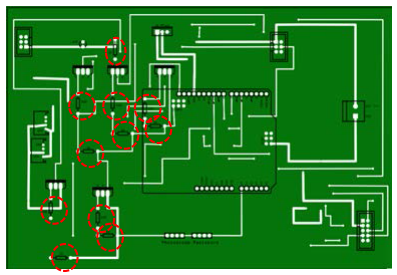
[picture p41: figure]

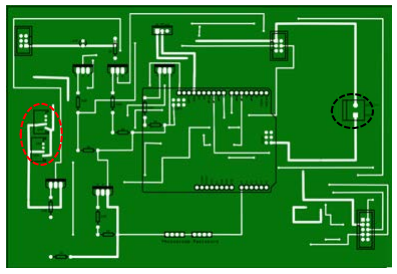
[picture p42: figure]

5. Solder the 4-pin JST-headers from the JST connector kit (#E12) to its positions (red dashed circles). There are two headers.
6. Solder the 2-pin screw-terminal header (#E23) to its position (black dashed circle). There is one header.

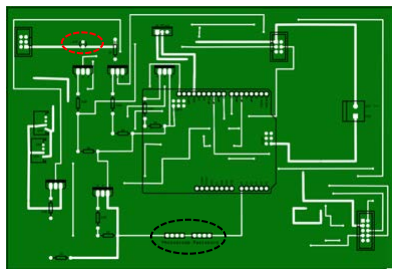
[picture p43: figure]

7. Solder the 0.1uF capacitor (#E25) to its position (red dashed circle). There is one
capacitor.
8. Solder two 4-pin female headers (#E22) to their positions (both within the black dashed line). Insert 100Mohm resistors into each of these headers. These serve as load resistors for the photodiode.

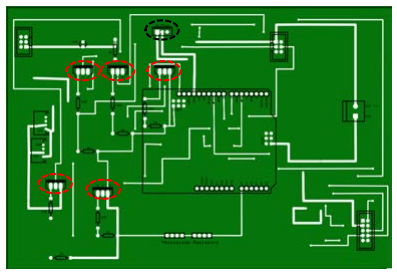
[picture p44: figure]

9. Solder all the MOSFETs (#E15) to the positions (red dashed circles) with orientation matching the silkscreen labels. There are five
MOSFETs.
10. Solder the 5V regulator (#E16) to its position (black dashed circle) with orientation matching the silkscreen labels. There is one 5V
regulator.

# LED Connection Board

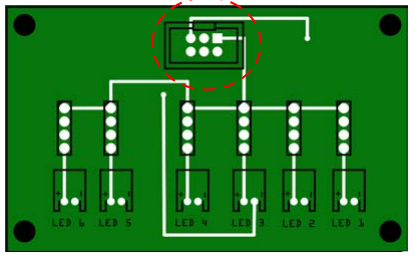
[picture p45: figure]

1. Solder the 2x3 IDC header (#E17) (red dashed
circle) with the orientation matching the silkscreen labels.

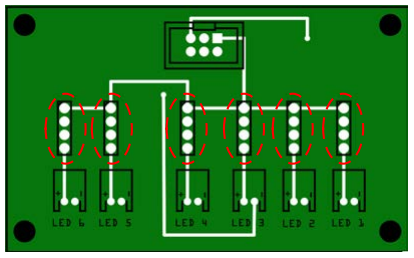
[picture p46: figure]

2. Solder the 4-pin female headers (#E22) (red dashed circles). Place a resistor into each of the headers based on specific amperage needs for the LEDs to be used, given a 12V supply. Recommended values are:
LED 1-3 (built-in excitation sources) - 330 ohm LED 4 (auxiliary source) - 330 ohm
LED 5 (TOP White Light) - 330 ohm
LED 6 (TOP Violet Light) - 470 ohm

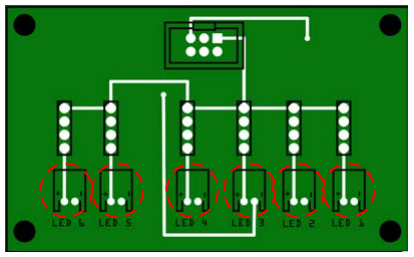
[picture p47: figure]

3. Solder the 2-pin JST headers from the JST connector set (#E12) (red dashed circles).

Numbers refer to Parts List numbering. This board decouples the excitation source connections from the main board.

# Power Switch Board

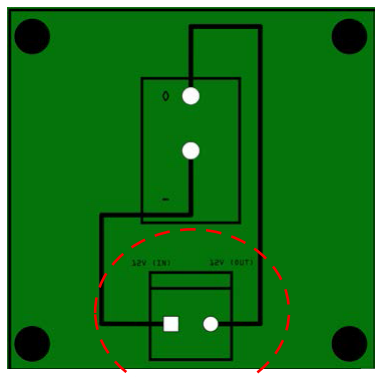
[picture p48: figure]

1. Solder the 2-pin screw terminal block (#E23) to its position (red dashed circle), with its orientation matching the silk screen.

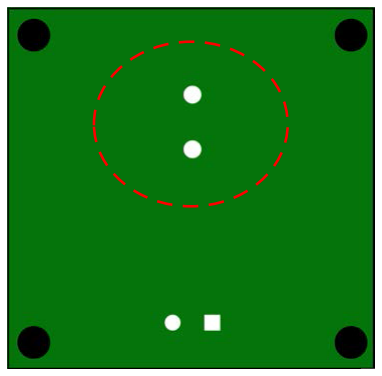
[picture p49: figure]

2. Flip the board over. Solder the rocker switch (#E19) to the back of the PCB in its position (red dashed circle), with its pins matching the corresponding silk screen on the front side.

Numbers refer to Parts List numbering

# Photodiode Board

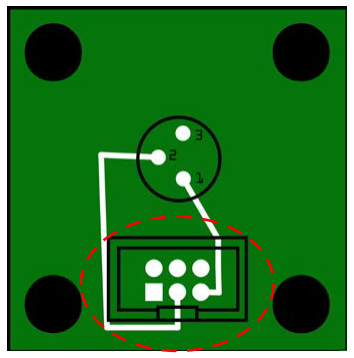
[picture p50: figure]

1. Solder the 2x3 IDC connector (#E13) to the front of the PCB in its position (red dashed circle). with orientation matching the silk screen. Numbers on the silkscreen correspond to the pin numbers of the photodiode specification sheet.
2. Place the photodiode (#O19) into the Thorlabs photodiode mount (#O13)

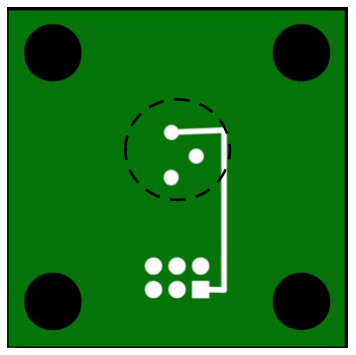
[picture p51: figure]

3. Flip the PCB over. Solder the photodiode to its position (black dashed circle).

Numbers refer to Parts List numbering

# Photodiode Mount Assembly

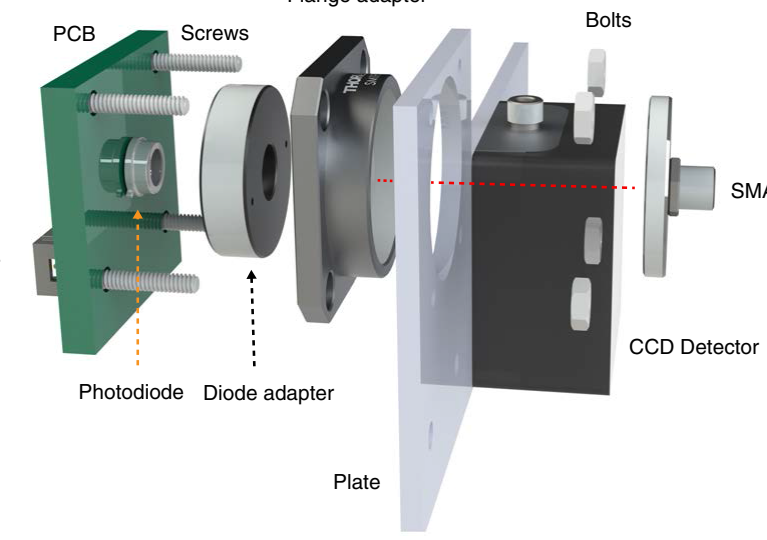
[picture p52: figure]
PCB; Photodiode; Diode adapter; Screws; Bolts; Plate; CCD Detector

Pin header

Flange adapter

SMA adapter

Numbers refer to Parts List numbering

[Skip to Step 4 if you have constructed the Photodiode board already]

1. Solder the 2x3 pin header (#E13) onto the photodiode PCB (#E29).
2. Place the photodiode (#O19) through the photodiode adapter (#O13).
3. Solder the photodiode to the PCB (#E29) such that the photodiode adapter is flush with the PCB.
4. Place the photodiode adapter and PCB assembly into the SM1-to-Flange adapter (#O21). The diode adapter should be inserted into the back end of the flange adapter. (side without the flange).
5. Place the SM1-to-SMA adapter (#O12) into the flange of the SM1-to-Flange adapter.
6. Place the entire SM1-to-Flange adapter into the acrylic wall mount (#L12) as shown above, and fix it into place with screws and hex nuts (#F29, F28).

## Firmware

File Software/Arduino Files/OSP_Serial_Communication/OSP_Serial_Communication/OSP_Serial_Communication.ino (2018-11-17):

#include <Servo.h> 

// MOTOR Inialization Setup
#define MOTORY 9        
#define MOTORX 5    
#define LINEARY_MIN  1000    
#define LINEARY_MAX  2000
#define LINEARX_MIN  1000   
#define LINEARX_MAX  1780  

Servo MotorX, MotorY;

// System Inialization Setup
String protocolString = "";
boolean protocolWait = false;
String parsedString = "";
int startIndex = 0;

bool positionFound = false;
int MotorXPosition = 1450;
int MotorYPosition = 1200;
int rowTop = 0;
int rowBottom;
int colRight = 0;
int colLeft;
double lightInput;
int startY = 1215;
int startX = 1450;
int newX = 0;
int newY = 0;
int currentX = 0;
int timeWait = 10000;
int dpx = 0;
int dpy = 0;

String ledString = "";
String auxString = "";
int auxDuration = 0;
int brightInt = 0;
long brightValue = 0;
long expTime = 0;
int pumpNumb = 0;
int pumpDur = 0;
String totalString = "";

void setup() {
  Serial.begin(9600);
  MotorY.attach(MOTORY , LINEARY_MIN, LINEARY_MAX);  // attaches/activates the linear actuator as a servo object 
  MotorX.attach(MOTORX , LINEARX_MIN, LINEARX_MAX);  // attaches/activates the linear actuator as a servo object
  MotorX.writeMicroseconds(1200);
  MotorY.writeMicroseconds(1200);
  currentX = 1200;
  pinMode(12, OUTPUT);
  pinMode(11, OUTPUT);
  pinMode(10, OUTPUT);
  pinMode(8, OUTPUT);
  pinMode(7, OUTPUT);
  pinMode(6, OUTPUT);
  pinMode(4, OUTPUT);
  pinMode(2, OUTPUT);
}

void loop() {
//  Serial.println("pass");
  if (Serial.available() > 0) {
    protocolString = Serial.readString();
    Serial.println(protocolString);
    for (int i = 0; i <= protocolString.length(); i++){ // Analyze command string one character at a time
      parsedString = protocolString.substring(i,i+1); 
      if (parsedString == ";"){ // ';' Symbolizes the end of a command
        // Command Key:
        // -------------------------------------------------------------
        // L - Signifies the command to toggle an LED.
        //     Followed by and INTEGER representing the LED Index to toggle.
        //        i.e. The command 'L1;' would toggle the LED in index 1
        // A - Signifies the command to trigger an Auxiliary port
        //     Followed by INTEGER representing the LED Index, as well as the duration to keep port triggered for.
        //        i.e. The command 'A490000;' would trigger the auxiliary LED for 90 s
        // -------------------------------------------------------------
        // C - Signifies the command to perform a step from the calibration protocol
        //     Followed by a LETTER representing the step which to perform and then an INTEGER representing 
        //     whether the plate has 24 wells or 96 wells.
        //     Calibration Step Key:
        //        F - Find Limits: This finds the bottom, top, left & right boundaries of the plate as well 
        //            as the step size between wells (dpx & dpy)
        //              i.e. CF; Performs the step. 
        //        T - Tune Center: This goes to the specified well position and tunes the center position by 
        //            finding the boundaries of the well and calculating the horizantel and vertical midpoints.
        //            Followed by the center position to tune.
        //              i.e. CT1060.001160.00; This would move the Motor X to position 1060.00 and Motor Y to 
        //                   position 10160.00 and perform the tuning step.
        //        P - Signifies the command to get the current Photodiode value
        //              i.e. CP; Performs the step.
        // -------------------------------------------------------------
        // M - Signifies the command to move both motors to the specified positions. 
        //     Followed by the X position and then the Y position as a float value with 2 decimal places.
        //     Motor values can be anywhere from 1000 to 2000 for MOTOR Y, and anywhere from 1000 to 1780 
        //     for MOTOR X. 
        //        i.e. M1060.001160.00; This will move Motor X to position 1060.00 and Motor Y to position 1160.00
        // -------------------------------------------------------------
        // S - Signifies the command to move both motors in a shaking pattern
        //
        if (protocolString.substring(startIndex, startIndex+1) == "L"){
          totalString = protocolString.substring(startIndex,i);
          Serial.println(totalString.length());
          if (totalString.length() <= 2){
            ledString = protocolString.substring(startIndex+1,i);
            if (ledString == "5"){
              digitalWrite(6, !digitalRead(6));
              }
            else if (ledString == "1"){
              digitalWrite(8, !digitalRead(8));
              
              }
            else if (ledString == "2"){
              digitalWrite(7, !digitalRead(7));
              }
            else if (ledString == "3"){
              digitalWrite(4, !digitalRead(4));
              }
            else if (ledString == "4"){
              digitalWrite(2, !digitalRead(2));
              }
          }
          else if (totalString.length() > 2){
            ledString = protocolString.substring(startIndex+1,i);
            if (ledString.substring(0,1) == "1"){
              digitalWrite(8, !digitalRead(8));
              Serial.println("LED 1 ON");
            }
            if (ledString.substring(1,2) == "1"){
              digitalWrite(7, !digitalRead(7));
              Serial.println("LED 2 ON");
            }
            if (ledString.substring(2,3) == "1"){
              digitalWrite(4, !digitalRead(4));
              Serial.println("LED 3 ON");
            }            
          }
          Serial.println("done");           
          }
        if (protocolString.substring(startIndex, startIndex+1) == "A"){
          totalString = protocolString.substring(startIndex,i);
          auxString = protocolString.substring(startIndex+1,startIndex+2);
          auxDuration = (protocolString.substring(startIndex+2,i)).toInt();
          if (auxString == "1"){
            digitalWrite(10, HIGH);
            delay(auxDuration);
            digitalWrite(10, LOW);
            }
          else if (auxString == "2"){
            digitalWrite(8, !digitalRead(8));
            digitalWrite(7, !digitalRead(7));
            digitalWrite(4, !digitalRead(4));
            delay(auxDuration);
            digitalWrite(8, !digitalRead(8));
            digitalWrite(7, !digitalRead(7));
            digitalWrite(4, !digitalRead(4));
//            digitalWrite(11, HIGH);
//            delay(auxDuration);
//            digitalWrite(11, LOW);            
            }
          else if (auxString == "3"){
            digitalWrite(12, HIGH);
            delay(auxDuration);
            digitalWrite(12, LOW);     
            }
          else if (auxString == "4"){
            digitalWrite(2, HIGH);
            delay(auxDuration);
            digitalWrite(2, LOW);     
            }
          Serial.println("done");           
          }
         else if (protocolString.substring(startIndex, startIndex+1) == "C"){
          if (protocolString.substring(startIndex+1, i-1) == "F"){
              MotorY.writeMicroseconds(1450);
              MotorYPosition = 1450;
              if (protocolString.substring(startIndex+2, i) == "1"){
                  MotorX.writeMicroseconds(1450);
                  MotorXPosition = 1450;
               }
              else if (protocolString.substring(startIndex+2, i) == "2"){
                  MotorX.writeMicroseconds(1425);
                  MotorXPosition = 1425;
               }
              delay(5000);
              rowTop = findRow("TOP");
              MotorY.writeMicroseconds(1150);
              MotorYPosition = 1150;
              if (protocolString.substring(startIndex+2, i) == "1"){
                  MotorX.writeMicroseconds(1450);
                  MotorXPosition = 1450;
               }
              else if (protocolString.substring(startIndex+2, i) == "2"){
                  MotorX.writeMicroseconds(1425);
                  MotorXPosition = 1425;                  
               }
              delay(5000);
              rowBottom = findRow("BOTTOM");
              MotorY.writeMicroseconds(1325);
              MotorX.writeMicroseconds(1550);
              MotorYPosition = 1325;
              MotorXPosition = 1550;
              delay(5000);
              colRight = findCol("RIGHT");
              MotorXPosition = startX;
              MotorY.writeMicroseconds(1250);
              MotorX.writeMicroseconds(1150);
              MotorYPosition = 1220;
              MotorXPosition = 1150;
              delay(5000);
              colLeft = findCol("LEFT");
              MotorXPosition = startX;
              MotorY.writeMicroseconds(startY);
              MotorX.writeMicroseconds(startX);
              if (protocolString.substring(startIndex+2, i) == "1"){
                dpy = (rowTop - rowBottom)/3.0;
                dpx = (colRight - colLeft)/5.0;
               }
              else if (protocolString.substring(startIndex+2, i) == "2"){
                dpy = (rowTop - rowBottom)/7.0;
                dpx = (colRight - colLeft)/11.0;
               }
              Serial.print(dpx);
              Serial.print(";");
              Serial.print(dpy);
              Serial.print(";");
              Serial.print(rowTop);
              Serial.print(";");
              Serial.print(rowBottom);
              Serial.print(";");
              Serial.print(colLeft);
              Serial.print(";");
              Serial.println(colRight);
            }
            else if(protocolString.substring(startIndex+1, startIndex+2) == "T"){
              newX = protocolString.substring(startIndex+2,i-4).toInt();
              newY = protocolString.substring(startIndex+6,i).toInt();
              MotorX.writeMicroseconds(newX);
              MotorY.writeMicroseconds(newY);
              delay(7000);
              int centerX = calculateHorizontalCenter(newX, newY);
              delay(2000);
              MotorX.writeMicroseconds(centerX);
              MotorY.writeMicroseconds(newY);
              delay(2000);
              int centerY = calculateVerticalCenter(centerX, newY);
              delay(2000);
              MotorX.writeMicroseconds(1200);
              MotorY.writeMicroseconds(1200);
              delay(3000);
              MotorX.writeMicroseconds(centerX);
              MotorY.writeMicroseconds(centerY);
              Serial.print(centerX);
              Serial.print(';');
              Serial.println(centerY);                            
            }
          }
        else if(protocolString.substring(startIndex, startIndex+1) == "M"){
          newX = protocolString.substring(startIndex+1,i-7).toInt();
          newY = protocolString.substring(startIndex+8,i).toInt();
          int search_valX = 645-(((newX - 1000.00)/1000.00)*645);
          int search_valY = 645-(((newY - 1000.00)/1000.00)*645);
          MotorX.writeMicroseconds(newX);
          MotorY.writeMicroseconds(newY);
          int waitX = 1;
          int waitY = 1;
          int old_X = analogRead(A5);
          int old_Y = analogRead(A4);
          int feedback_X;
          int feedback_Y;
          int count_X = 0;
          int count_Y = 0;
          while((waitX == 1) || (waitY == 1)){
            feedback_X = analogRead(A5);
            feedback_Y = analogRead(A4);
            if((feedback_X < old_X+2) && (feedback_X > old_X - 2)){
               count_X += 1;
               if(count_X == 5){
                waitX = 0;
               }
               
            }
            if((feedback_Y < old_Y+2) && (feedback_Y > old_Y - 2)){
               count_Y += 1;
               if(count_Y == 5){
                waitY = 0;
               }
            }
            old_X = feedback_X;
            old_Y = feedback_Y;
            delay(150);
          }
          Serial.println("done");
        }
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

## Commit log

2018-11-14 Update README.md
    Added link to biorxiv pre-print.
2018-11-15 Potential fix to mac arduino registration
2018-11-17 Added CAD Files & Laser Cut files
    [96well_plate.SLDPRT, L1 - Front Floor.DWG, L1 - Front Floor.SLDPRT, L10 - Y-Axis Motor Floor.DWG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]
2018-11-17 Added fritzing files and gerber .zip files for production
    [LED_CIRCUIT.fzz, MAINPOWER.fzz, PHOTODIODE_CIRCUIT.fzz, POWERSWITCH_BOARD.fzz]
2018-11-17 Cleaned up arduino script
2018-11-17 Fixed arduino script motor feedback recognition
2018-11-18 Added folder for assemblies
    [L11 - Primary Electronics Mount.DWG, L11 - Primary Electronics Mount.SLDPRT, LED_CIRCUIT.fzz, PHOTODIODE_CIRCUIT.fzz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]
2018-11-18 Added Raspberry Pi Image folder
2018-11-19 Updated parts
    [L12 - Detector Wall Mount.DWG, L12 - Detector Wall Mount.SLDPRT]
2019-04-19 Added .STL files of all .SLDPRT files. All .SLDPRT files were updated to be in inches.
    [96well_plate.SLDPRT, L1 - Front Floor.STL, L10 - Y-Axis Motor Floor.DWG, L10 - Y-Axis Motor Floor.SLDPRT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]
2019-05-13 handle adjustment
    [L6 - Right Panel Door.DWG, L6 - Right Panel Door.SLDPRT, L6 - Right Panel Door.STL, L7 - Front Panel Door.DWG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]
